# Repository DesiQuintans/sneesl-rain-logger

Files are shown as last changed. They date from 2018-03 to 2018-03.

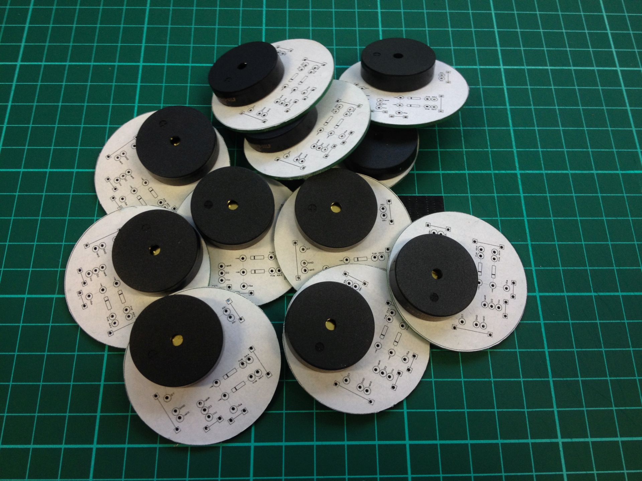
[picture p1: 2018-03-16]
Build notes/Photos/IMG_3371_developed.jpg

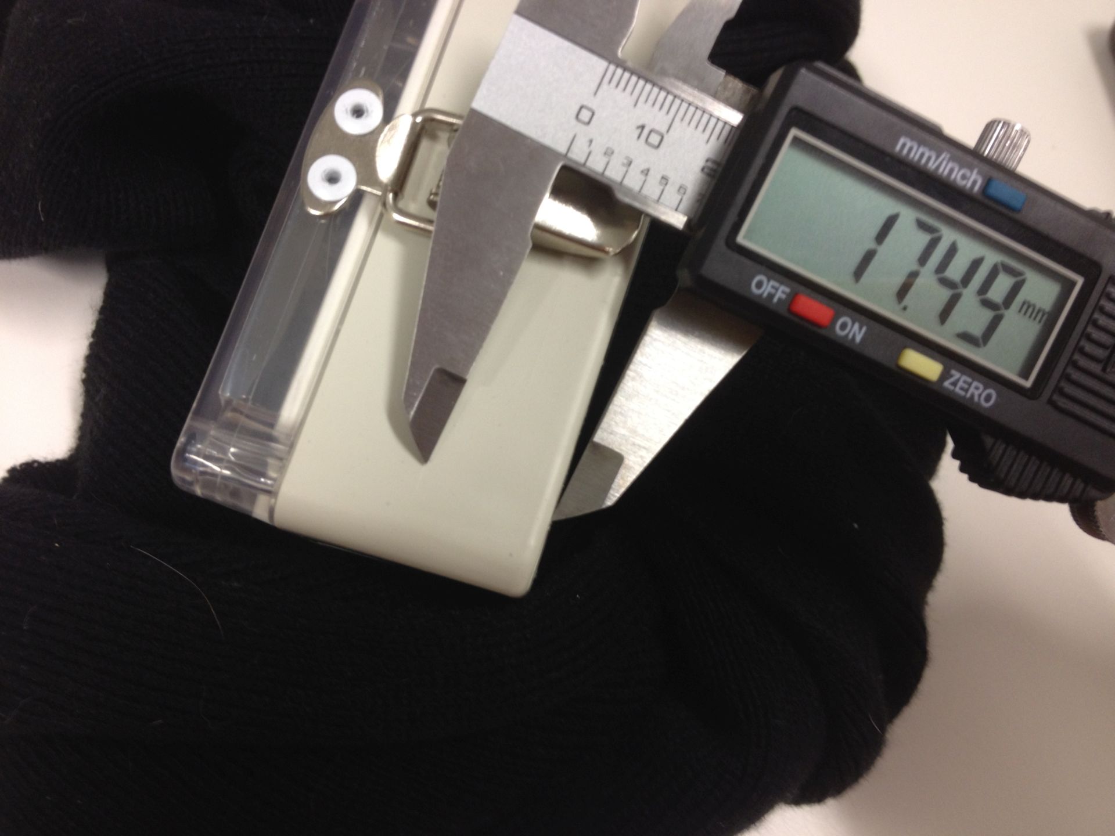
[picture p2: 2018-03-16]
Build notes/Photos/IMG_3365.JPG

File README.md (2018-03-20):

# Sneesl, a TinyDuino-based data-logger for rain collectors

## What is _Sneesl_?

**Sneesl** <sup>1</sup> is a battery-powered data-logging device built on [the TinyDuino plaform](https://tinycircuits.com/pages/tinyduino-overview), designed to record pulses from a tipping-bucket rain collector. These rain collectors are basically large funnels that drain into two small scoops, set back-to-back on a central pivot. When the scoop is full, it tips over and empties itself, raising the other scoop so that it can fill up. The 'tipping over' motion passes a magnet over a reed switch, which is detected and recorded by Sneesl.

Notes and BOM for building a Sneesl data-logger can be found in `Building Sneesl.md`.

Information about how Sneesl works and what kind of data it outputs can be found in `Using Sneesl.md`.

## License and citation

I dedicate Sneesl to the public domain. If you use it for scientific work, please cite:

> Quintans, DJ 2015. Sneesl: An Arduino-based data-logger for rain collectors. Microprocessor software. https://github.com/DesiQuintans/sneesl-rain-logger. doi:10.5281/zenodo.1204674

## Features that Sneesl has

- **6+ months battery life from easy-to-find AA batteries.** It takes 6 batteries in a parallel 3×2 configuration for redundancy. In practice I have sometimes left Sneesl in the field for 9+ months, but I prefer to maintain them more regularly.
- **Data storage on microSD.** MicroSD cards are relatively cheap and are reliable for field use. They can be read in the field using a tablet or laptop, so you can pull down the data without having to bring the logger back to the lab or having to use an expensive reader.
- **Integrated battery life checks.** Sneesl ensures that the battery's voltage is stable enough to safely write data to the SD card. It also records battery life as part of the logging process.
- **Power-On Self-Test.** Sneesl uses a buzzer to warn you if something is wrong (e.g. SD card inserted incorrectly, battery voltage low, unknown problem with the circuit), so that you know the logger is okay before you leave the field site.
- **Input-agnostic pulse counting.** If you have any kind of sensor that uses a switch closure as the response, Sneesl can log it.
- **Timed events.** Sneesl does its logging at regular intervals using a real-time clock, so you can modify it to do things like read a humidity/temperature sensor regularly too.

## Features that Sneesl *does not* have

- Since the number of input channels on an Arduino is limited, Sneesl is not the best choice for multiplexing lots of sensors.
- Sneesl could probably do remote monitoring by using a phone or GSM module to transmit information, but I have not tried to actually implement it here.

## Resources included in this repository

- `Build notes/` contains information about actually building Sneesl.
  - `Bill of materials/` contains a parts list with approximate prices.
  - `Circuits/` has the circuit diagrams. Always use the newest one.
  - `Digital logbook/` is mostly me talking to myself inside text files throughout the development process.
  - `Photos/` has unsorted photos of the development, testing, and assembly process.
- `Firmware/` contains the Arduino code for the loggers.
  - `08_LoggerV8/` is a version of `V7` that has some changes to its comments and formatting.
  - `07_LoggerV7/` is the version I have deployed in the field.
  - `06_LoggerV6/`
  - `05_LoggerV5/`
  - `04_Datalogger_TinyDuino/`
  - `03_BareMetal_TinyDuino/`
  - `02_BareMetal_TD_2/`
  - `01_Datalogger/` is the first version, it ran on $1 Arduino Nano clones with extra modules.
- `_Bench testing/` has enclosure tests, visualisations of data, and battery life predictions.
- `_Scratchpad/` contains code that I used during Sneesl's development process.
  - `INTERRUPTS/` was used for prototyping the wake-up process.
  - `LOW POWER/` was used for prototyping the deep-sleep process.
  - `RTC/` is used to set and get Real-Time Clock modules.
  - `SD/` was for testing different SD card readers before I settled on TinyDuino.
  - `SENSORS/` is test code for photocells (to record brightness) and DHT11 sensors (temperature and humidity) which I omitted from the production run of Sneesl.

---

1: _Sneesl_ is [a Scottish word for raining lightly](http://scottishsceptic.co.uk/2014/11/28/scots-more-words-for-rain-than-eskimos-for-snow/).

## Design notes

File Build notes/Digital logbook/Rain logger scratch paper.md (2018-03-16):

# Logging rain gauge #project

## Use case ##
This device will be placed in the field and allowed to log rain data for at least 1 year and a maximum of 3 years.

## Requirements ##
1. Uses a common battery type like AA or 9 V, allowing for global field resupply.
2. Has a battery life of at least one year.
3. Records rainfall in mass/hour (1 mm == 1 kg per m^2 per hour). The recommended resolution of 0.2 mm is therefore 200 mL per hour.
4. Chassis and moving parts built from off-the-shelf materials with a minimum of hand-working.

## Mathing it up ##
For a 20 cm funnel:

      π x r^2
    = π x 0.1^2 m
    = 0.0314159 m^2 funnel area.

      1 m^2 / funnel area
    = 31.8309886 scaling factor (# funnels inside 1 m^2)

By multiplying a list of potential tipping weights with my scaling factor above, we can find how many mm of rain each bucket tip records. With a 20 cm funnel, 1 mm of rain roughly corresponds with a tip weight of 32 g. With a 10 cm funnel, it corresponds to 8 g (exact numbers in spreadsheet).

## Prototype materials list ##

### From the dollar store ###
| Qty | Item                           | Cost (AUD) |
|-----|--------------------------------|-----------:|
| 1   | Smart-Link 'Store Jar' large   | 2.50       |
| 1   | SAS Automotive 4 pc funnel set | 2.00       |
| 1   | Homeware Hardware 20 cm funnel | 2.00       |
| 2   | Party Central 4 pk candy scoop | 6.00       |
| 1   | Eagiestar 'Epoxy Steel'        | 2.00       |
|     |                                |            |
|     |                      **Total** | **14.50**  |

### From Bunnings ###
| Qty | Item                        | Cost (AUD) |
|-----|-----------------------------|-----------:|
| 1   | 36" of 3/16" threaded rod   | 03.00      |
| 1   | 3/16" bolt and nut 22 pc set| 04.00      |
| 1   | 3/16" brass washer 25 pc set| 03.32      |
|     |                             |            |
|     |                   **Total** | **10.32**  |

## Equipment list ##

### From the dollar store ###
| Qty | Item                | Cost (AUD) |
|-----|---------------------|-----------:|
| 1   | Butane pencil torch | 06.00      |
| 1   | Mini hacksaw        | 03.00      |
| 1   | Mini hacksaw blades | 02.00      |
|     |                     |            |
|     | **Total**           | **11.00**  |

## Order of actions ##
1. Cut off the bottom of the jar with a standard disposable-blade cutter. Discard cut-off.
2. Cut off the handles from two candy scoops with mini hacksaw. File the cut down until level with the scoop body. Discard cut-off handles.
3. Scoop bodies need to be joined to make the double-sided bucket. I'll try Plastimake. A hole for the pivot axle can also be made inside the Plastimake, combining two jobs into one.
    1. First, make a template to ensure that the scoops can be joined at a repeatable angle (40°). Cut three squares from corrugated cardboard, cut a 50° wedge out of each square, and then glue them all face-to-face with epoxy. Cover the cut faces with duct tape; this is your spacer mould.
    1. Soften 5 grams of Plastimake in boiling water. When soft, place it into newly-boiled water to get it as hot as possible. Quickly fold it into a cube, then force the cube into the mould to produce a wedge of Plastimake.
    1. While still soft, push a large nail through the Plastimake wedge from both sides, wiggling the nail to enlarge the hole. This is the hole for the axle.
4. When the wedge is completely solidified, drill out the hole to fit your axle loosely.
5. Soften the sides of the wedge by dipping briefly in boiling water, then press-fit onto the scoops to make the shape of the wedge conform to the shape of the scoop. If desired, the bond can be made stronger with epoxy.

**Wrong turn:** This design seems easy when you're looking at a bunch of scoops, but it's actually really tough to get the scoops centered and place the axle hole uniformly and so on. It took me basically 4 hours to figure out the scoops. Tomorrow I will buy some aluminum sheet (or some cans of soft drink!) and just scratch-make the bucket assembly.

**Another wrong turn:** The jar I bought is also too small. I will grab a PVC pipe and cap tomorrow too.

## Quick reference for rain logger maths ##

### Heaviest one-day rainfall in the world ###
2,493 mm (12,465 0.2 mm bucket tips, ~ 9 per min)

### Heaviest one-day rainfall in the Blue Mountains ###
285 mm (1,425 0.2 mm bucket tips, ~ 1 per min)

### SD card write time ballpark ###
Let's call it 0.01 ms to write 1 byte. Therefore the data string:

    2015-03-21T15:26:47    540\n(24 bytes)

Can be written in 0.24 ms.

### Milliseconds in 1 hour ###
3,600,000 ms

### List of power draws ###

| Board                  | State       | Current draw (mA) |
|------------------------|-------------|------------------:|
| Pro Mini               | Running     | 16.00             |
|                        | Sleeping    | 0.48              |
| MicroSD module         | Writing     | 1.47              |
|                        | Sleeping    | 1.34              |
| Real-Time Clock module | Reading     | ?                 |
|                        | Sleeping    | 1.70              |
| Fudge factor           | All states  | 1.00              |
|                        |             |                   |
| **Total**              | **Running** | **20.17**         |
|                        | **Sleeping**| **4.52**          |

The heaviest rain ever gave 540 tips per hour. At 0.23 ms per tip, that's 0.0000345 of each hour writing at 20.17 mA. That leaves 0.9999655 of each hour doing nothing at 4.52 mA.

Therefore, each hour drains:

			0.000695865 mA per hour writing
			4.519844060 mA per hour idling
	TOTAL = 4.520539925 mA per hour

Therefore, a 2400 mAh alkaline battery gives 530 hours of perfect operation (22 days). The numbers are basically identical for the Blue Mountains rainfall record.

So the biggest drain here is not the time spent running the program, but the time spent sleeping. Therefore my efforts should concentrate on getting idle drain as low as possible.

## Data logger costing ##

| Qty | Item                   | Supplier     |  Cost (AUD) |
|-----|------------------------|--------------|------------:|
| 12  | Davis rain collector   | DavisNet     |     1335.96 |
| 12  | AA battery holder      | LittleBird   |       12.96 |
| 12  | 5 V step-up module     | eBay         |       47.16 |
| 12  | Arduino Pro Mini 5 V   | LittleBird   |      141.00 |
| 12  | 5 x 7 cm proto board   | eBay         |       35.88 |
| 12  | Real-time clock module | eBay         |       44.04 |
| 12  | MicroSD module         | eBay         |       63.24 |
| 12  | 4 GB microSD card      | eBay         |       59.28 |
| 12  | Reed switch module     | eBay         |       45.72 |
| 12  | 64 x 58 x 35 mm box    | LittleBird   |       71.40 |
| 36  | Duracell AA batteries  | eBay         |       29.99 |
|     |                        |              |             |
|     |                        | **Total**    | **1886.63** |
|     |                        | **Fudged**   | **2000.00** |
|     |                        | **Per unit** |  **166.67** |

## Data logger flow ##

1.	Watchdog timer starts (poll every 6 minutes).
2.	Arduino goes to sleep.
3.	Water bucket tips, and a magnet on the bucket sweeps across a reed switch. Reed switch is connected to voltage, and to a digital input pin set up to interrupt sleep.
4.	When the reed switch closes, the digital pin is set high.
5.	Arduino wakes up due to high interrupt pin.
6.	Arduino increments an internal counter (TipCounter), and then goes back to sleep as quickly as possible.
7.	Meanwhile, watchdog timer is asking every 8 minutes:
	1. Does the RTC say that 1 hour has elapsed?
	2. If no, go back to sleep.
	3. If yes:
	    - Write TipCounter to the SD card with the date and time.
	    - Set TipCounter = 0
	    - How many seconds off from the hour is the watchdog? Set the next watchdog timers shorter to sync them.
	    - Go back to sleep.

## Things to do for data logger ##

### For 6 April 2015 ###

- ☑ Learn how to write to microSD.
	- Write:	SD	→	ReadWrite
- ☑ Learn how to set and get RTC.
	- Set:	Time	→	TimeSerial
	- Get:	DS1307RTC	→	ReadTest
- ☒ Learn how to use reed switch to set a pin high.
	- That actually doesn't work --- you need to set the pin low.
- ☑ Learn how to put Arduino to sleep and wake it up with the reed switch.
- ☑ Learn how to use a watchdog timer.
- ☑ Learn how to run an Arduino from 2x AA batteries.
- ☑ Learn how to run RTC from 2x AA batteries.
- ☑ Learn how to write to microSD from 2x AA batteries.

### For 10 April 2015 ###

- ☐ Learn how to measure milliamps with my cheapo multimeter.
	- Ahaha I blew the fuse, that's why I was having trouble.
	- ☑ Make a fixed-voltage power regulator to help me calculate current.
		- I made one with an LM317, Vout= 5.04V, R1=330R, R2=1000R.
- ☐ Experiment with different sleep modes to see if my code still works.
- ☑ Solder headers onto Arduino Pro Mini and Nanos.
- ☐ Transplant modules onto Pro Mini and see if everything works.
- ☐ Design protoboard layout.

## Data logger pinout ##

|         | Module | Arduino |
|---------|--------|---------|
| RTC     |        |         |
|         | Gnd    | GND     |
|         | VCC    | 5V      |
|         | SDA    | A4      |
|         | SCL    | A5      |
|         |        |         |
| MicroSD |        |         |
|         | Gnd    | GND     |
|         | VCC    | 5V      |
|         | MISO   | D12     |
|         | MOSI   | D11     |
|         | SCK    | D13     |
|         | CS     | D10     |

## File naming scheme ##

File names need to be 8 characters or fewer, which is poo. But anyway:

    123456789
    ---------
    20150410

A condensed date naming scheme works, I think, because of my backup strategy:

## Backup strategy ##

I will have one large log (LOGFILE.CSV) where all of my data is written. Every day, the contents of LOGFILE.CSV get dumped into a new file named with the YYYYMMDD.CSV scheme. If LOGFILE.CSV gets corrupted, then the daily dumps might still be alright!

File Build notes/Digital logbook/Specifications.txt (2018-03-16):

# Logging rain gauge #project

## Use case ##
This device will be placed in the field and allowed to log rain data for at least 1 year and a maximum of 3 years.

## Requirements ##
1. Uses a common battery type like AA or 9v, allowing for global field resupply.
2. Has a battery life of at least one year.
3. Records rainfall in mass/hour (1mm == 1kg per m^2 per hour). The recommended resolution of 0.2mm is therefore 200 mL per hour.
4. Chassis and moving parts built from off-the-shelf materials with a minimum of hand-working.

## Mathing it up ##
For a 20 cm funnel:

      π x r^2
    = π x 0.1^2 m
    = 0.0314159 m^2 funnel area.

      1 m^2 / funnel area
    = 31.8309886 scaling factor (# funnels inside 1 m^2)

By multiplying a list of potential tipping weights with my scaling factor above, we can find how many mm of rain each bucket tip records. With a 20cm funnel, 1 mm of rain roughly corresponds with a tip weight of 32 g. With a 10cm funnel, it corresponds to 8 g (exact numbers in spreadsheet).

## Prototype materials list ##

### From the dollar store ###
| Qty | Item                           | Cost (AUD) |
|-----|--------------------------------|-----------:|
| 1   | Smart-Link 'Store Jar' large   | 2.50       |
| 1   | SAS Automotive 4pc funnel set  | 2.00       |
| 1   | Homeware Hardware 20cm funnel  | 2.00       |
| 2   | Party Central 4pk candy scoop  | 6.00       |
| 1   | Eagiestar 'Epoxy Steel'        | 2.00       |
|     |                                |            |
|     |                      **Total** | **14.50**  |

### From Bunnings ###
| Qty | Item                        | Cost (AUD) |
|-----|-----------------------------|-----------:|
| 1   | 36" of 3/16" threaded rod   | 03.00      |
| 1   | 3/16" bolt and nut 22pc set | 04.00      |
| 1   | 3/16" brass washer 25pc set | 03.32      |
|     |                             |            |
|     |                   **Total** | **10.32**  |

## Equipment list ##

### From the dollar store ###
| Qty | Item                | Cost (AUD) |
|-----|---------------------|-----------:|
| 1   | Butane pencil torch | 06.00      |
| 1   | Mini hacksaw        | 03.00      |
| 1   | Mini hacksaw blades | 02.00      |
|     |                     |            |
|     | **Total**           | **11.00**  |

## Order of actions ##
1. Cut off the bottom of the jar with a standard disposable-blade cutter. Discard cut-off.
2. Cut off the handles from two candy scoops with mini hacksaw. File the cut down until level with the scoop body. Discard cut-off handles.
3. Scoop bodies need to be joined to make the double-sided bucket. I'll try Plastimake. A hole for the pivot axle can also be made inside the Plastimake, combining two jobs into one.
    1. First, make a template to ensure that the scoops can be joined at a repeatable angle (40°). Cut three squares from corrugated cardboard, cut a 50° wedge out of each square, and then glue them all face-to-face with epoxy. Cover the cut faces with duct tape; this is your spacer mould.
    1. Soften 5 grams of Plastimake in boiling water. When soft, place it into newly-boiled water to get it as hot as possible. Quickly fold it into a cube, then force the cube into the mould to produce a wedge of Plastimake.
    1. While still soft, push a large nail through the Plastimake wedge from both sides, wiggling the nail to enlarge the hole. This is the hole for the axle.
4. When the wedge is completely solidified, drill out the hole to fit your axle loosely.
5. Soften the sides of the wedge by dipping briefly in boiling water, then press-fit onto the scoops to make the shape of the wedge conform to the shape of the scoop. If desired, the bond can be made stronger with epoxy.

**Wrong turn:** This design seems easy when you're looking at a bunch of scoops, but it's actually really tough to get the scoops centered and place the axle hole uniformly and so on. It took me basically 4 hours to figure out the scoops. Tomorrow I will buy some aluminum sheet (or some cans of soft drink!) and just scratch-make the bucket assembly.

**Another wrong turn:** The jar I bought is also too small. I will grab a PVC pipe and cap tomorrow too.

## Quick reference for rain logger maths ##

### Heaviest one-day rainfall in the world ###
2,493 mm (12,465 0.2 mm bucket tips, ~ 9 per min)

### Heaviest one-day rainfall in the Blue Mountains ###
285 mm (1,425 0.2mm bucket tips, ~ 1 per min)

### SD card write time ballpark ###
Let's call it 0.01 ms to write 1 byte. Therefore the data string:

    2015-03-21T15:26:47    540\n(24 bytes)

Can be written in 0.24 ms.

### Milliseconds in 1 day ###
3,600,000 ms

### List of power draws ###

| Board                  | State       | Current draw (mA) |
|------------------------|-------------|------------------:|
| Pro Mini               | Running     | 16.00             |
|                        | Sleeping    | 0.48              |
| MicroSD module         | Writing     | 1.47              |
|                        | Sleeping    | 1.34              |
| Real-Time Clock module | Reading     | ?                 |
|                        | Sleeping    | 1.70              |
| Fudge factor           | All states  | 1.00              |
|                        |             |                   |
| **Total**              | **Running** | **20.17**         |
|                        | **Sleeping**| **4.52**          |

The heaviest rain ever gave 540 tips per hour. At 0.23 ms per tip, that's 0.0000345 of each hour writing at 20.17 mA. That leaves 0.9999655 of each hour doing nothing at 4.52 mA.

Therefore, each hour drains: 

			0.000695865 mA per hour writing
			4.519844060 mA per hour idling
	TOTAL = 4.520539925 mA per hour

Therefore, a 2400 mAh alkaline battery gives 530 hours of perfect operation (22 days). The numbers are basically identical for the Blue Mountains rainfall record.

So the biggest drain here is not the time spent running the program, but the time spent sleeping. Therefore my efforts should concentrate on getting idle drain as low as possible.

## Data logger costing ##

| Qty | Item                   | Supplier     |  Cost (AUD) |
|-----|------------------------|--------------|------------:|
| 12  | Davis rain collector   | DavisNet     |     1335.96 |
| 12  | AA battery holder      | LittleBird   |       12.96 |
| 12  | 5V step-up module      | eBay         |       47.16 |
| 12  | Arduino Pro Mini 5V    | LittleBird   |      141.00 |
| 12  | 5 x 7 cm proto board   | eBay         |       35.88 |
| 12  | Real-time clock module | eBay         |       44.04 |
| 12  | MicroSD module         | eBay         |       63.24 |
| 12  | 4GB microSD card       | eBay         |       59.28 |
| 12  | Reed switch module     | eBay         |       45.72 |
| 12  | 64 x 58 x 35 mm box    | LittleBird   |       71.40 |
| 36  | Duracell AA batteries  | eBay         |       29.99 |
|     |                        |              |             |
|     |                        | **Total**    | **1886.63** |
|     |                        | **Fudged**   | **2000.00** |
|     |                        | **Per unit** |  **166.67** |

## Data logger flow ##

1.	Watchdog timer starts (poll every 6 minutes).
2.	Arduino goes to sleep.
3.	Water bucket tips, and a magnet on the bucket sweeps across a reed switch. Reed switch is connected to 	voltage, 
        and to a digital input pin set up to interrupt sleep.
4.	When the reed switch closes, the digital pin is set high.
5.	Arduino wakes up due to high interrupt pin.
6.	Arduino increments an internal counter (TipCounter), and then goes back to sleep as quickly as possible.
7.	Meanwhile, watchdog timer is asking every 8 minutes:
	1. Does the RTC say that 1 hour has elapsed?
	2. If no, go back to sleep.
	3. If yes:
	    - Write TipCounter to the SD card with the date and time.
	    - Set TipCounter = 0
	    - How many seconds off from the hour is the watchdog? Set the next watchdog timers shorter to sync them.
	    - Go back to sleep.

## Things to do for data logger ##

- ☑ Learn how to write to microSD.
	- Write:	SD	→	ReadWrite
- ☑ Learn how to set and get RTC.
	- Set:	Time	→	TimeSerial
	- Get:	DS1307RTC	→	ReadTest
- ☒ Learn how to use reed switch to set a pin high.
	- That actually doesn't work --- you need to set the pin low.
- ☑ Learn how to put Arduino to sleep and wake it up with the reed switch.
- ☑ Learn how to use a watchdog timer.
- ☑ Learn how to run an Arduino from 2x AA batteries.
- ☑ Learn how to run RTC from 2x AA batteries.
- ☑ Learn how to write to microSD from 2x AA batteries.

### For 10 April 2015: ###
- ☐ Learn how to measure milliamps with my cheapo multimeter.
- ☐ Experiment with different sleep modes to see if my code still works.
- ☐ Solder headers onto Arduino Pro Mini.
- ☐ Transplant modules onto Pro Mini and see if everything works.
- ☐ Design protoboard layout.

## Data logger pinout ##

|         | Module | Arduino |
|---------|--------|---------|
| RTC     |        |         |
|         | Gnd    | GND     |
|         | VCC    | 5V      |
|         | SDA    | A4      |
|         | SCL    | A5      |
|         |        |         |
| MicroSD |        |         |
|         | Gnd    | GND     |
|         | VCC    | 5V      |
|         | MISO   | D12     |
|         | MOSI   | D11     |
|         | SCK    | D13     |
|         | CS     | D4      |

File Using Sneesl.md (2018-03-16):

# Using and maintaining Sneesl

## Diagnostic buzzer sounds

### Error sounds

**3 beeps, each the same pitch**
Low battery voltage, or circuit error. Replace the batteries and/or check the circuit for loose or shorted wires.

**2 beeps, one short and one long, each the same pitch**
SD card access error. The card couldn't be accessed or written to. Remove the batteries and then try removing and reinserting the SD card.

### All-okay sounds

**Four notes, rising pitch**
Power-On Self-Test found no problems, the logger is now ready for input. Tip the buckets manually to confirm that they move freely before leaving the site.

**Single beeps**
Played when a bucket tip is detected and added to the running count. A higher-pitched version is played when the running count is recorded to the logfile.

## Logged data format

By default, Sneesl writes to the logfile hourly in this format:

| Time                | Tips | mV   | Event  |
|---------------------|------|------|--------|
| 2016-12-24T12:29:07 | 0    | 4483 | Reboot |
| 2016-12-24T13:00:00 | 0    | 4630 | Normal |
| 2016-12-24T14:00:00 | 0    | 4278 | Normal |
| 2016-12-24T15:00:00 | 3    | 4295 | Normal |
| 2016-12-24T16:00:00 | 7    | 4295 | Normal |
| 2016-12-24T17:00:00 | 34   | 4295 | Normal |
| 2016-12-24T18:00:00 | 16   | 4278 | Normal |
| 2016-12-24T19:00:00 | 3    | 4395 | Normal |
| 2016-12-24T20:00:00 | 0    | 4611 | Normal |
| 2016-12-24T21:00:00 | 0    | 4593 | Normal |

- `Time` is in ISO-8601 format for easy parsing with software.
- `Tips` is the number of bucket tips recorded in the preceding hour. My buckets hold 0.2 mm of rain, so the rainfall experienced between 4 and 5 PM is `34 × 0.2 = 6.8 mm`.
- `mV` is the estimated voltage available at the time of recording. Note that because this is a (very) rough estimation, the values fluctuate quite a bit. This fluctuation is accounted for in Sneesl's voltage checking function.
- `Event` marks the type of log written. _Reboot_ events are written during POST and should be omitted from your results.

## Maintaining Sneesl

- Keep the data loggers dry and sheltered. Mine fit inside the rain collector's housing, which is very convenient.
- Make sure that the wire leading to the data logger does not interfere with the motion of the buckets.
- I had several instances where dust and debris clogged the rain collector and stopped all readings. It pays to check your collectors regularly during the rainy season to make sure this isn't happening.
- Be careful of spiders that make their homes inside the rain collector.
- RTC units can drift by a few minutes over the course of a year. If this is a problem, you should bring in your Sneesl units once a year to update their internal clocks and/or replace the RTC's onboard batteries.

## Program logic

### Power-On Self-Test

1. The user inserts batteries. Sneesl will run on 3x AA batteries, but it is best to provide 6 AA batteries so that there is a redundant power supply option.
2. Sneesl estimates the available battery voltage.
  - If voltage is <3200 mV, the batteries are discharged below an experimentally-derived safety limit. Below this level, the TinyDuino may randomly 'brownout' and reading/writing to the SD card may destroy the stored data.
  - In case of low voltage, Sneesl will use the buzzer to play an insistent error sound (three identical notes, looping). This error sound will also play if there is error in the circuit that interferes with Power-On Self-Test, like a loose wire.
3. If voltage is above the safety limit, Sneesl tries to create a new logfile (if one doesn't exist already) and then tries to write a new observation to the file (marked as a 'Reboot' event).
  - If logfile creation or writing fail, then Sneesl's buzzer will play an SD warning sound (short-long, short-long — imagine it's saying, "Ess Dee! Ess Dee!").
4. Sneesl sets an alarm telling it when to wake up (by default, `RTC.setAlarmRepeat(EVERY_HOUR);`), and then goes into deep sleep to save power.

### In the event of rain

1. If the rain collector's bucket is tipped, the pulse created by the switch wakes Sneesl.
2. Sneesl checks its voltage again, making sure that it is safe to write to the Arduino's onboard memory.
3. The bucket tip is added to a running count.
4. Sneesl goes back to sleep.

### When the alarm goes off

1. The RTC alarm wakes Sneesl.
2. It checks its voltage again to make sure that it is safe to access the SD card.
3. Sneesl records the number of bucket tip events that it counted since the last alarm (marked as a 'Normal' logging event). A confirmation sound is played.
4. The running count is cleared and Sneesl goes back to sleep.

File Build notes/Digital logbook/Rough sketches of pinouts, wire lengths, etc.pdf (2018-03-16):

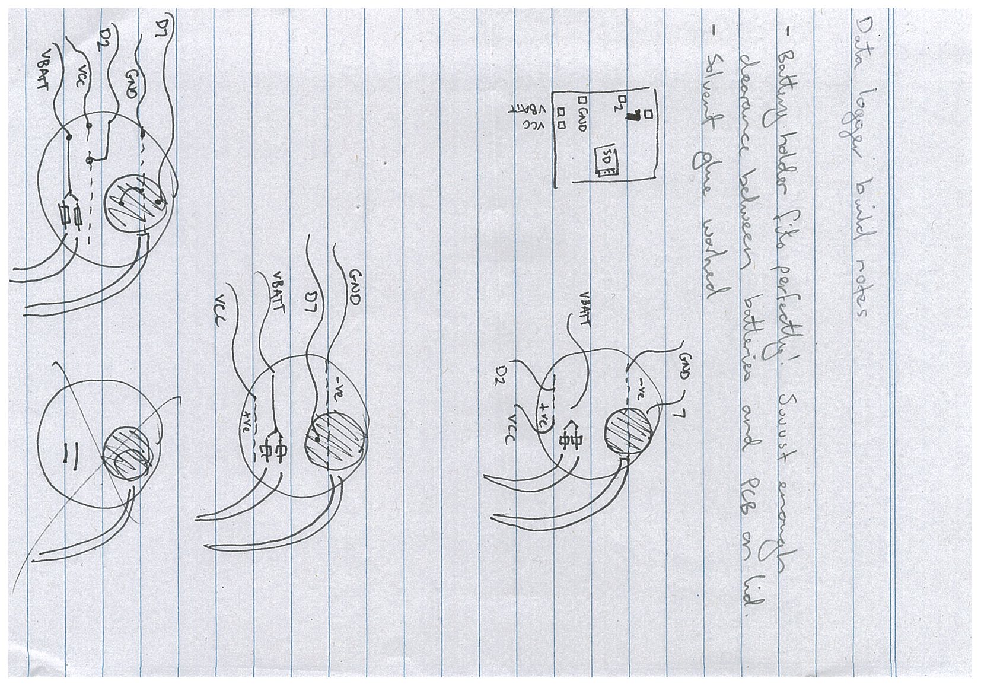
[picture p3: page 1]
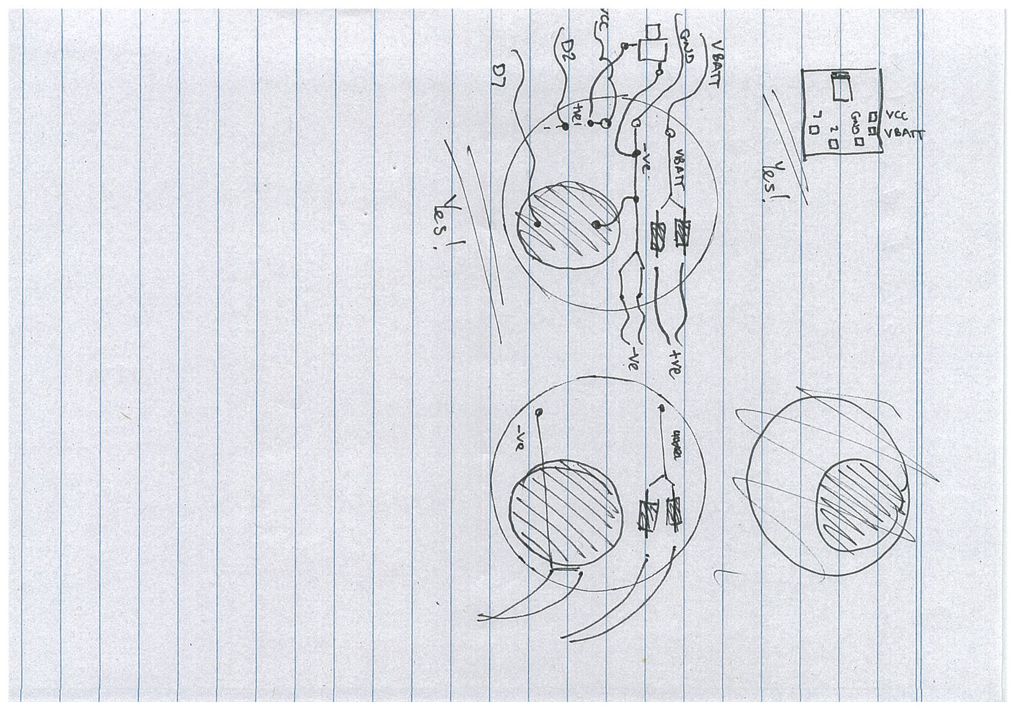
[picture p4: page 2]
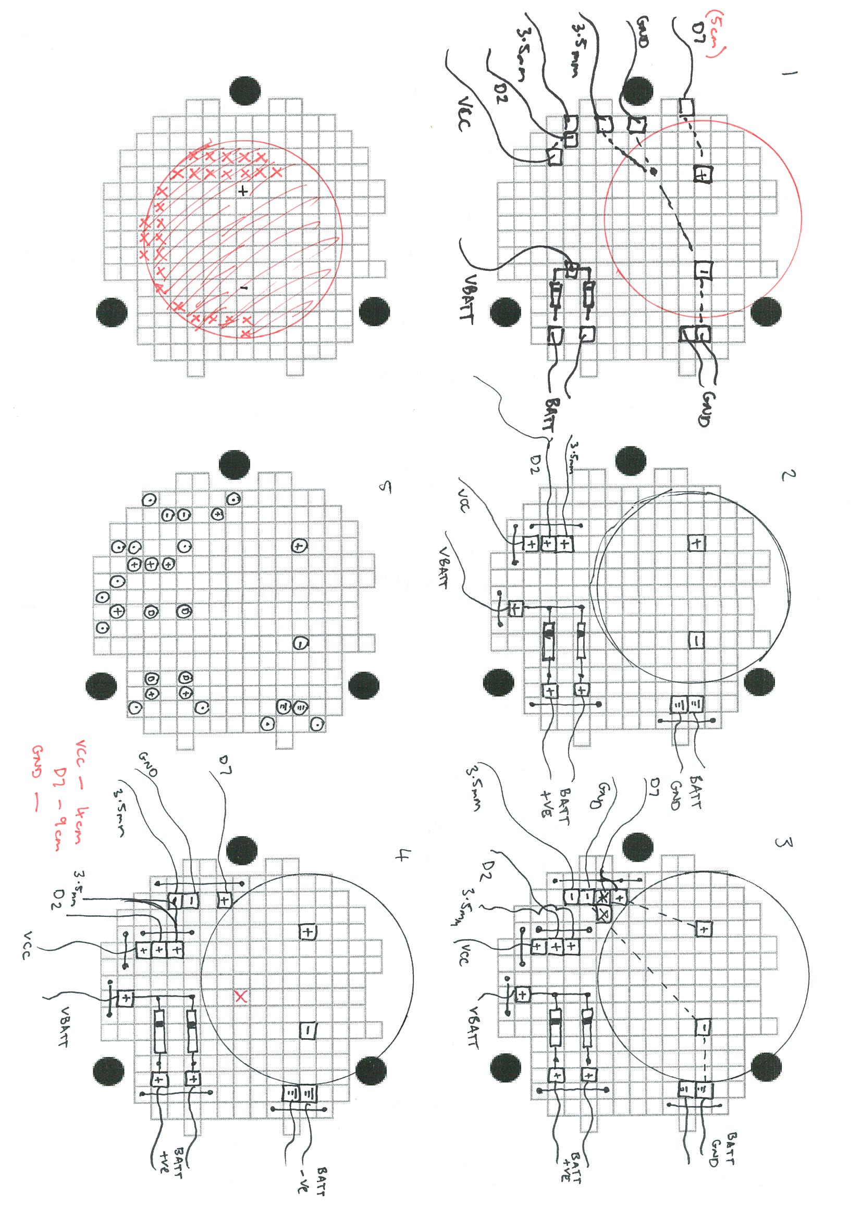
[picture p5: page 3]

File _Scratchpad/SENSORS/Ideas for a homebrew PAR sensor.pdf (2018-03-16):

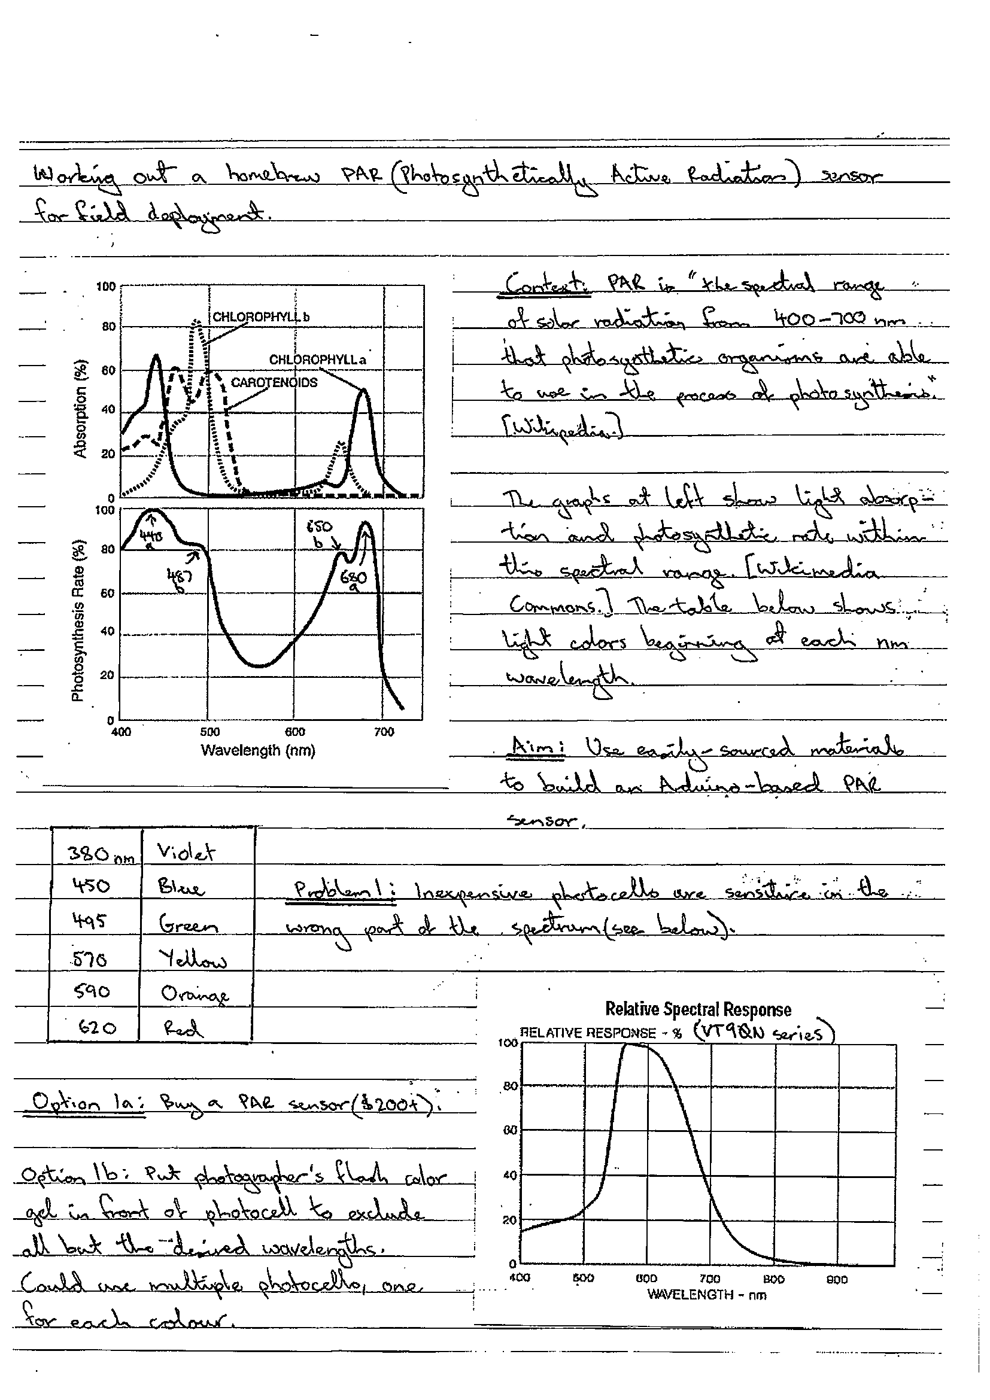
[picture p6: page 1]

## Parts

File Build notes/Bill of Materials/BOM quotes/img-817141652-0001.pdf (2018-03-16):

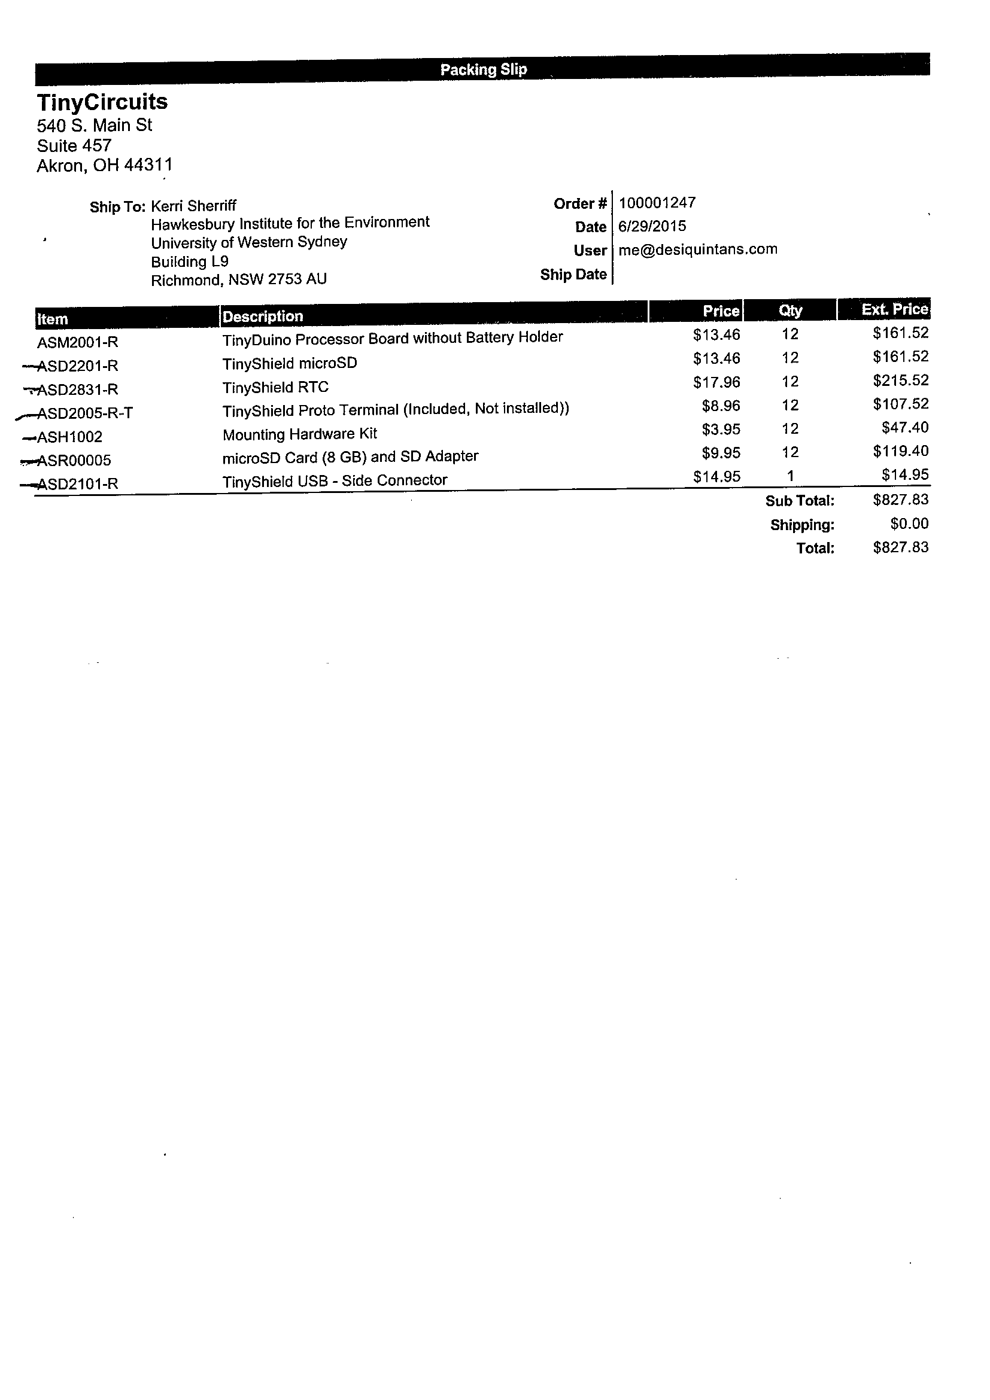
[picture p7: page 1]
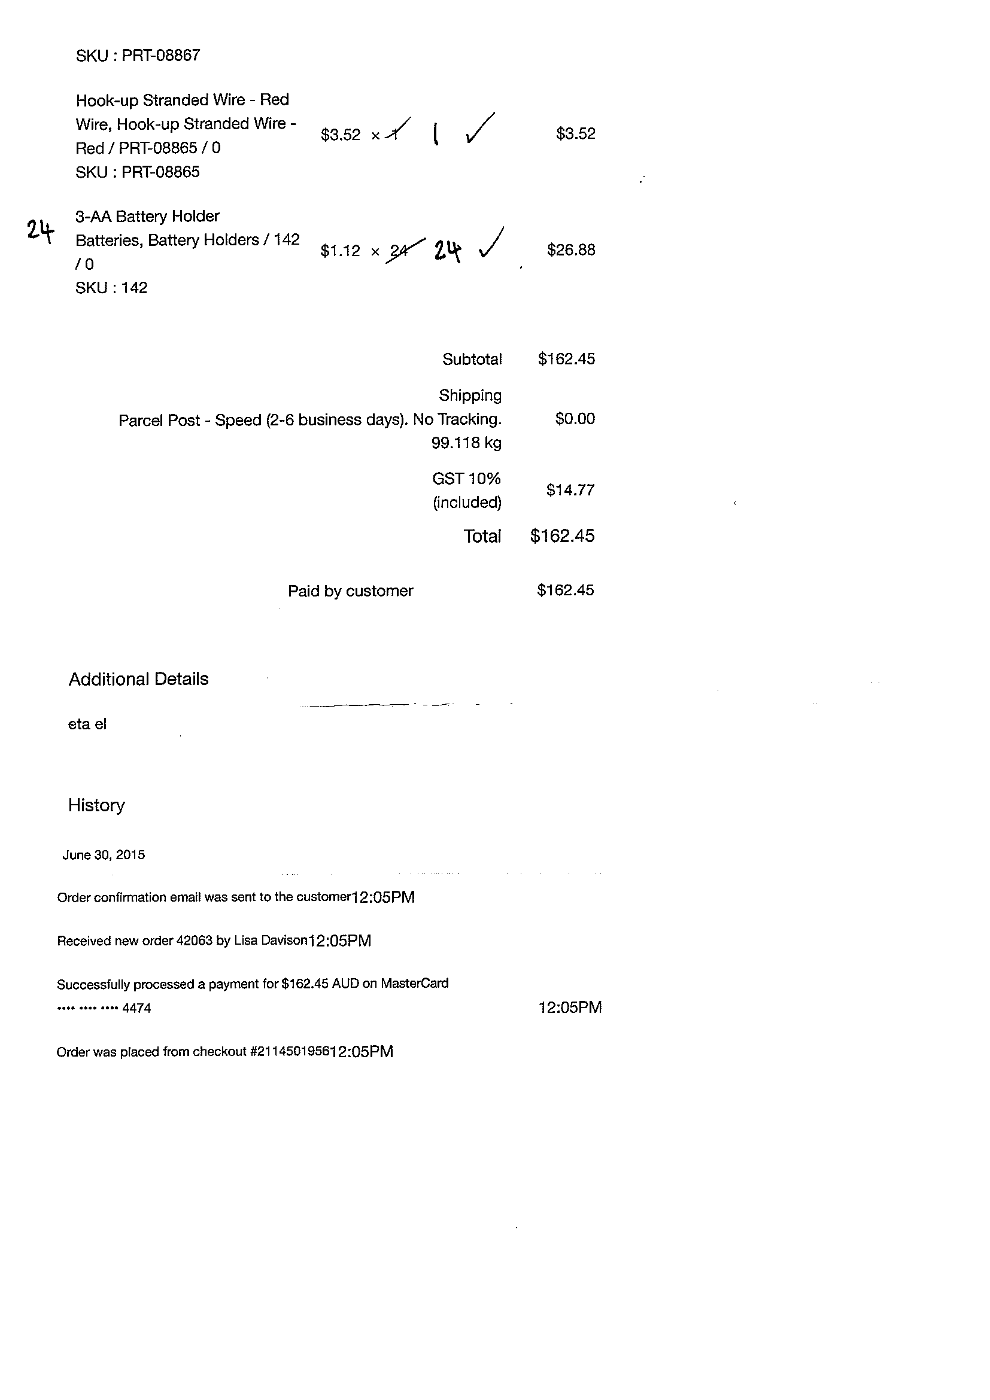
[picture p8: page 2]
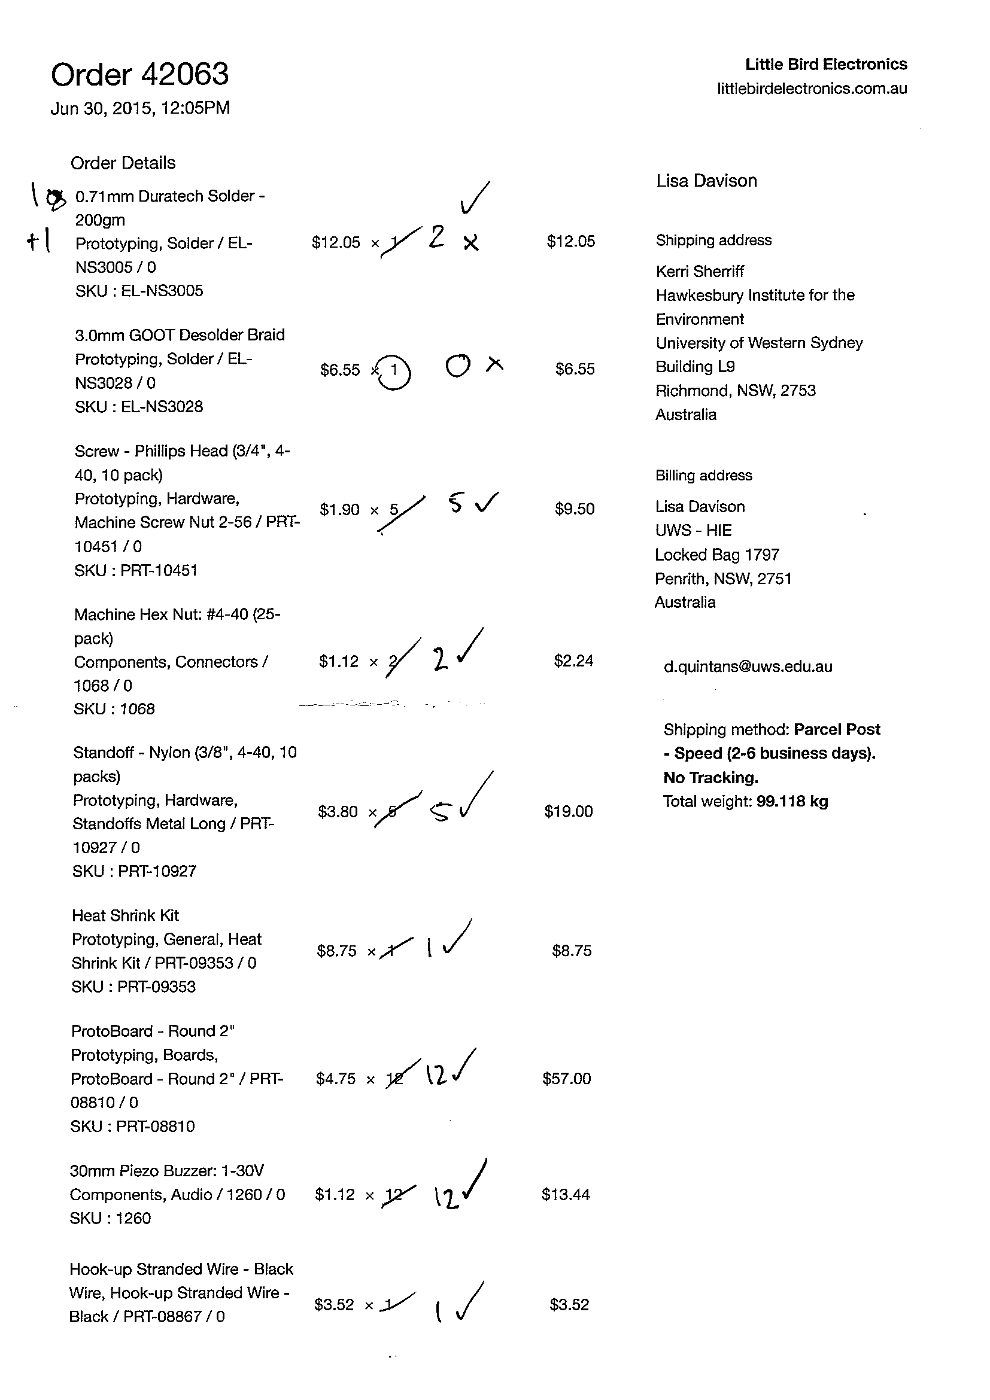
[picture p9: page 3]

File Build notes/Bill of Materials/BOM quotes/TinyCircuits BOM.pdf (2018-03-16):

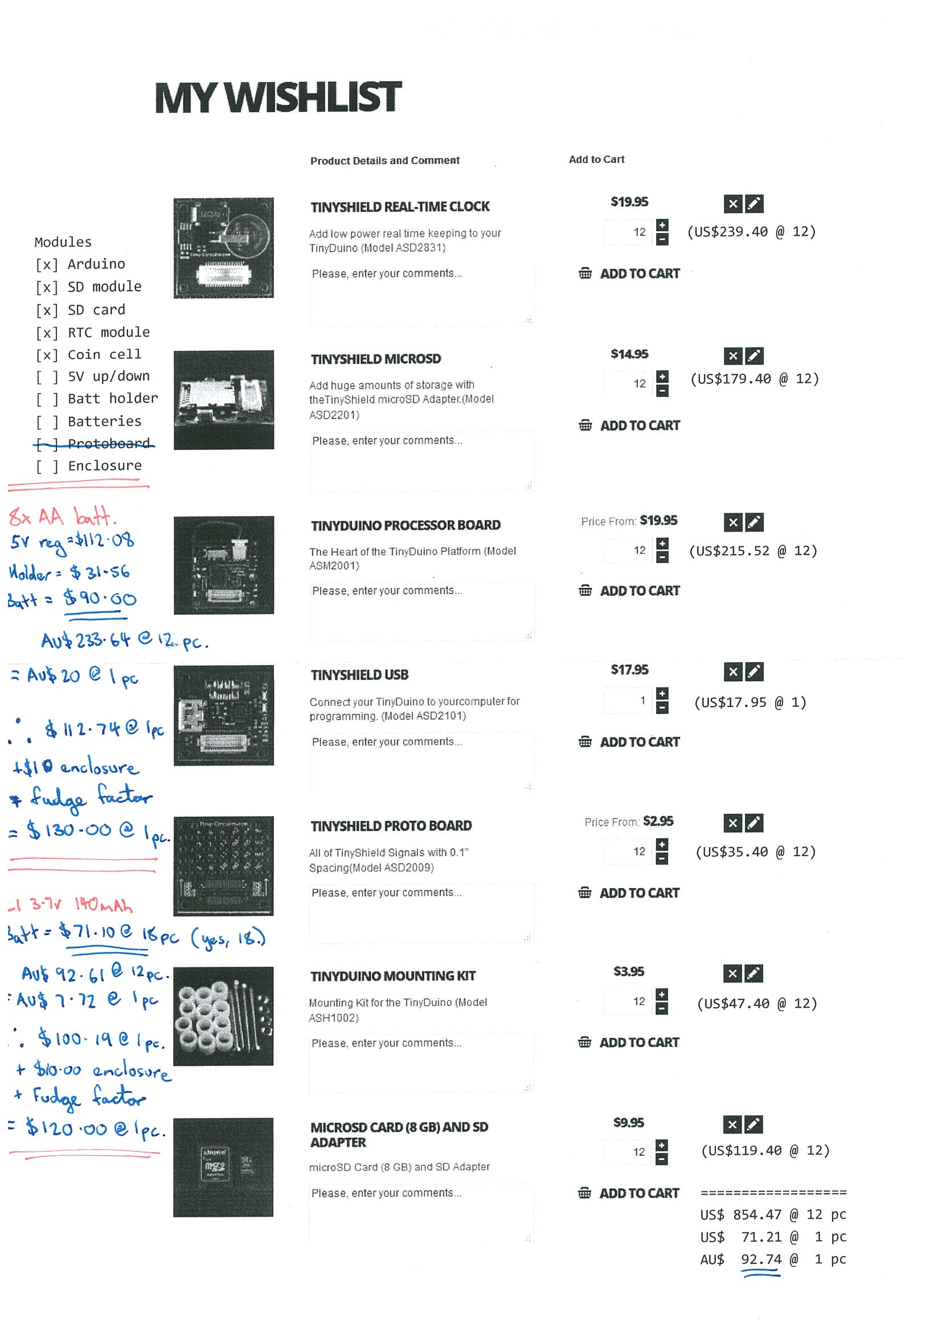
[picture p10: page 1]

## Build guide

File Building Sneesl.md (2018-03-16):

# Building a Sneesl data logger

These notes assume that you have basic experience with assembling and soldering an electronic circuit, as well as connecting and programming an Arduino.

## Materials for 1x Sneesl

| Pieces | Object                                  | Source            | Rounded cost (AUD)   |
| ------ | --------------------------------------- | ----------------- | -------------------- |
|        | **Exterior:**                           |                   |                      |
| 1      | Davis tipping-bucket rain collector     | Davis Instruments | 150.00               |
| 1      | Waterproof enclosure, 100×68×50 mm      | AliExpress        | 3.00                 |
| 1      | Spring-loaded toggle latch, 27 mm       | AliExpress        | 1.00                 |
| 4      | Pop rivets for latch                    | Hardware store    | 1.00                 |
|        |                                         |                   | 155.00 (Total)       |
|        | **TinyDuino modules:**                  |                   |                      |
| 1      | Processor board w/o battery holder      | TinyCircuits      | 14.00                |
| 1      | TinyShield MicroSD                      | TinyCircuits      | 14.00                |
| 1      | TinyShield RTC                          | TinyCircuits      | 18.00                |
| 1      | TinyShield Proto Terminal               | TinyCircuits      | 9.00                 |
| 1      | Mounting hardware kit                   | TinyCircuits      | 4.00                 |
| 1      | MicroSD card (8GB) *                    | TinyCircuits      | 10.00                |
| 1      | TinyShield USB (side connector) *       | TinyCircuits      | 15.00                |
|        |                                         |                   | 84.00 (Total)        |
|        | **Assorted electronics:**               |                   |                      |
| 2      | Diode, 1N5819                           | AliExpress        | 1.00                 |
| 1      | Resistor, 4.7k ohms                     | AliExpress        | 1.00                 |
| 1      | Through-hole piezo buzzer               | AliExpress        | 1.00                 |
| 1      | 3.5 mm jack (male/female panel-mount) * | AliExpress        | 1.00                 |
| 1      | Prototyping board (cut to size)         | AliExpress        | 1.00                 |
| 2      | 3x AA battery holders                   | AliExpress        | 1.00                 |
| 6      | AA batteries (decent ones) *            | Reject Shop       | 2.00                 |
|        |                                         |                   | 8.00 (Total)         |
|        | **Other consumables:**                  |                   |                      |
|        | Solid-core and braided wire             |                   |                      |
|        | Solder                                  |                   |                      |
|        | Soldering braid                         |                   |                      |
|        | Printable adhesive labels               |                   |                      |
|        |                                         |                   | 247.00 (Grand total) |

**Re. microSD cards:** I bought the cards from TinyCircuits so that I didn't have to worry about compatibility or counterfeiting. If you want to source your own SD cards, try to find cards that are 1-16 GB in size, since these tend to be more reliable with Arduinos.

**Re. the TinyShield USB programmer:** You only need to buy one or two of these; the USB programmer is not deployed in the field with the rest of the stack.

**Re. the 3.5 mm jack:** You can use any **normally open** connector you want, I just had a lot of 3.5 mm jacks on hand. You *could* wire the rain collector into the logger directly, but it's very convenient to be able to separate them.

**Re. AA battery holders:** Some holders come with an exposed length of wire at the back, linking the cells together. It's smart to cover this wire with tape so that it doesn't short with anything.

**Re. AA batteries:** I can buy a 50-pack of Eveready AA batteries for $12 from my local Reject Shop branch (it's a seconds store). These batteries haven't leaked in any of my 12 loggers, even when the temperature fluctuates from 0–45 °C. I guess you could use rechargeables, but then you add the mental load of having to make sure the new batteries are properly charged. The downside of using disposable batteries is that every 6 months when I replace the batteries, I am left with 72 batteries that are only one-quarter discharged.

## Circuit diagram

Please see `Build notes/Circuits/` to find circuit diagrams. The .fzz format is openable with [Fritzing](http://fritzing.org). If you don't have Fritzing, you can look at the .png format version.

## Build photos and tips

Please see `Build notes/Photos/` for mixed photos of the build process that could be helpful. If you browse the documents in `Build notes/Digital logbook/` could also be instructive.

## Programming Sneesl

### Library dependencies

- [rocketscream's Low-Power](https://github.com/rocketscream/Low-Power)
- [sridharrajagopal's DSRTCLib](https://github.com/sridharrajagopal/DSRTCLib)

### General notes

You can use the Arduino IDE to program Sneesl.

1. Use `_Scratchpad/RTC/Set_RTC_Time` to set the time on the TinyDuino's RTC (real-time clock) shield. Compile the script and then upload it immediately (because it sets the RTC based on the compile time of the script).
2. Compile and upload the latest Sneesl firmware from `Firmware/`.

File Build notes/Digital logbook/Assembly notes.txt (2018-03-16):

# 11 Aug 2015 #

Things I'm happy with:

	* The battery holder fits perfectly! Juuuuust enough clearance between the top of the batteries and the top of the buzzer on the overturned PCB.
	* The spring clasps are amazeballs. So handy already.
	* The PCB and TinyDuino are sized perfectly to fit into the lid. Mounting with double-sided tape is simple and secure.
	* Using terminal screw-posts is great because the wires can be flattened against the lid. Using pins or soldering them onto the protoshield would make them stick out at least a little.
	* Battery wires on the right side of the PCB is fine. There's a hollow on the right of the battery pack that they can nestle into.

Things I'm neutral about:

	* The wires going from the PCB to the TinyDuino are quite rigid. However, a good side of this is that once the PCB and TinyDuino are mounted, the wires can be pushed down and will stay put by themselves.
	* The TinyDuino is mounted so that the wires make sense, but you need to sort of dig in between the wires coming out of the PCB to get the SD card out. If I flip it 180° the GND and D2 wires would be incredibly short, but the SD card will easy to grab from the edge of the lid.

Things I'm unhappy with:

	* The lid looks uninteresting from the outside because everything is mounted upside-down.
	* The logger label covers the TinyDuino, which is more visually interesting than the PCB (for now).
	* Over-torquing the face screw of the 3.5 mm jack can cause it to shear apart! Do not over-tighten. Countersinking the front face so that the nut sits inside the material should give me a more positive (and glue-able!) attachment.
	* The wires coming off the PCB and to the components in the case body (battery packs and 3.5 mm jack) need to be tidied up with braided cable covering. The battery and 3.5 mm should be done separately, so that the battery packs can be removed independently.
	* The logger reads a tip event whenever something conductive touches the closed 3.5 mm jack's contacts. 
	* Pull-up resistor can probably be removed from the PCB, using the built-in pull-up instead.
	* The 3.5 mm jack needs to be mounted so that it's easier to fit from the inside.
	* The cord for the 3.5 mm jack is too short.

Things to add and change:

	* A silica bag can be placed on the left side, both to cushion the battery pack and prevent movement, as well as to protect the internals. Need to find the indicator silica!
	* Can I mount the PCB right-side-up by using cut-down standoffs? Is it worth it? Maybe for just one photo-op logger?
	* 
		* If I don't mount the PCBs right-way–up, I can move the top-face labels so that they cover the middle of the PCB and make it look less boring.

	* Add braided cable cover to battery and 3.5 mm jack wires — or tidy up in some other way. Short lengths of shrink wrap? Tiny zip ties?
	* 
		* But should not interfere with the battery pack's fit into the enclosure!

	* Can I change the 3.5 mm jack/plug to fix the false readings?
	* 3.5 mm jack cables need to be made as long as the battery pack cables.
	* Countersink the face of the 3.5 mm mounting hole.

# 12 Aug 2015 #

After trying some of the proposed changes:

	* Mounting the PCB right-side-up is not worth it, because it increases complexity and makes an already-cramped build more cramped.
	* Braided cable is a bit of a job, but zip ties or shrink wrap work just fine for binding the wires together.
	* The 3.5 mm plug cannot be changed; it will always trigger when plugging in a jack, regardless of what wiring I try. Will simply catch it during data quality control (filter out <1 mm of rain within an hour).
	* 3.5 mm jack cables are now 15 cm long. They could still stand to be longer, perhaps 20 cm for the one that needs to reach longer.
	* I tried mounting the TinyDuino rotated 180° so that the SD card would be against the edge of the lid, reasoning that this would make it easier to grab. It actually makes it more difficult, because the lid prevents you from getting your finger underneath the card. When the card is adjacent to the PCB, there's enough room to do that.
	* Countersinking the 3.5 mm jacks was unnecessary; Simply super-gluing them into the hole and finger-tightening the locking nut is good enough.

# 31 Aug 2015 #

☑ Mount spring clasps onto boxes.
☑ Drill rain jack mounting holes.
☑ Solder wires to rain jacks, then heatshrink.
☑ Clip mounting studies off the bottoms of the boxes.
☑ Glue 3x AA holders back-to-back.
☑ Make first PCB prototype.
☑ Revise PCB layout and make PCB guide labels.
☑ Affix guide labels to remaining PCBs.
☑ Make changes to Arduino software: logging period and internal pull-up resistor.
☑ Prep battery wires and rain jack wires with short lengths of heatshrink to keep them tidy in the box.
☒ Make breadboard test-bed for PCB components (to test functionality before soldering).
     ☒ Test all battery pack combinations (pack A only, pack B only, both packs in parallel) to ensure they work.
     ☒ Test with rain collector hooked into the circuit.
☑ Populate PCBs with buzzer, diodes, and rails.
☑ Pre-cut wire lengths for PCBs.
☑ Solder all components and wires.
☑ Add strain relief staples.
☐ Assemble TinyDuinos.
☐ Set TinyDuino time.
☐ Program TinyDuinos with newest software.
☐ Hook up PCBs to TinyDuinos, trimming wires to fit.
☑ Glue and screw rain jacks to boxes.

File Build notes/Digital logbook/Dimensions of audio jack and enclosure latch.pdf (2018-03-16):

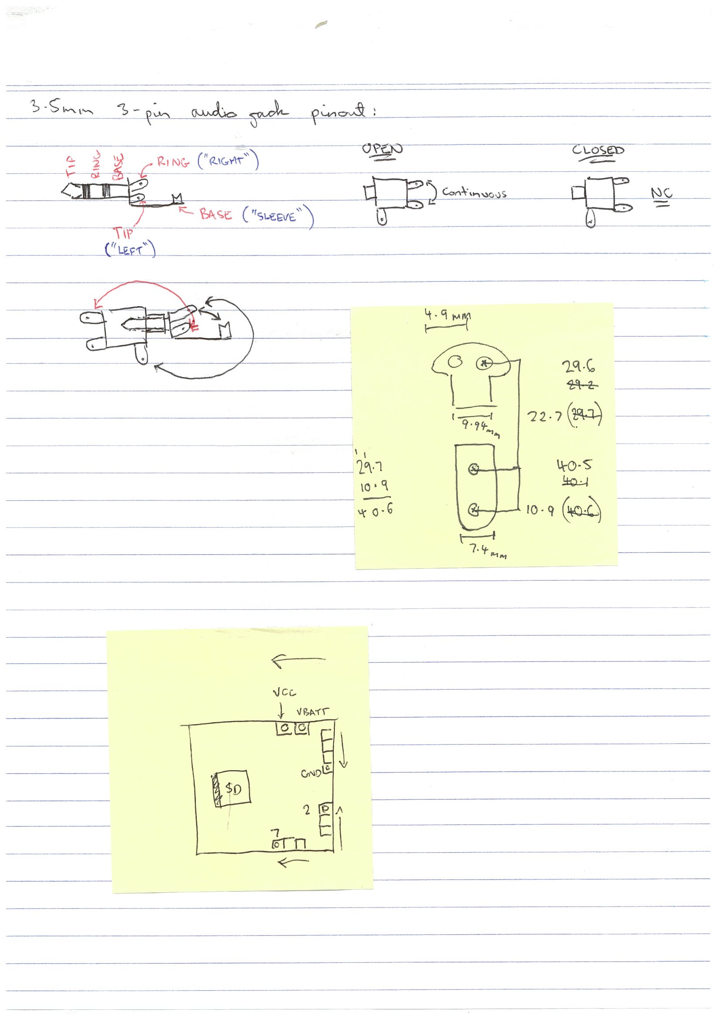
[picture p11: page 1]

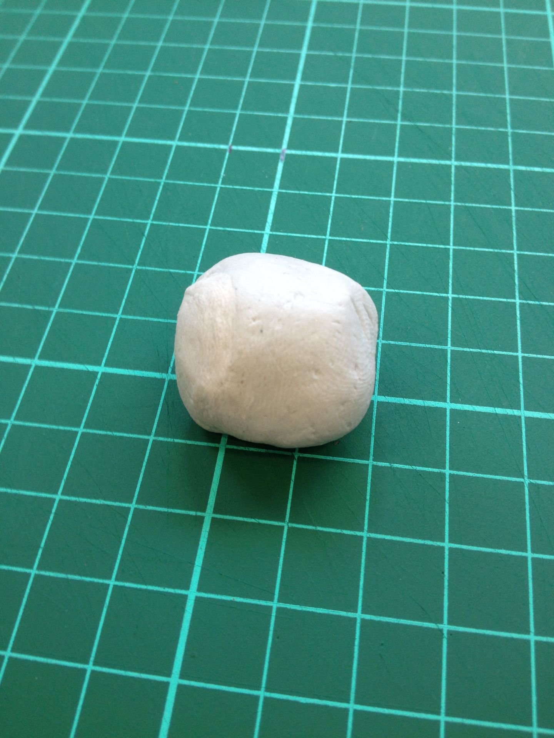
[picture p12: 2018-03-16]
Build notes/Photos/Photo 17-08-2015 11 25 43.jpg

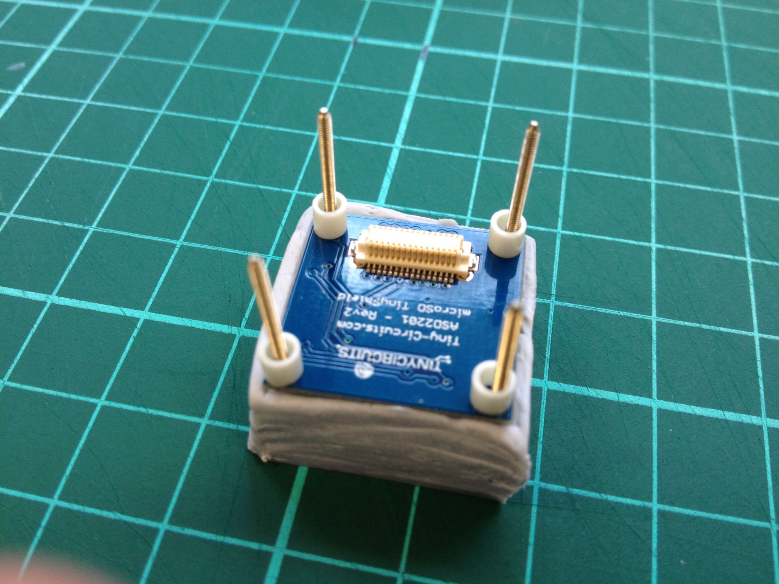
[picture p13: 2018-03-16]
Build notes/Photos/Photo 17-08-2015 11 46 45.jpg

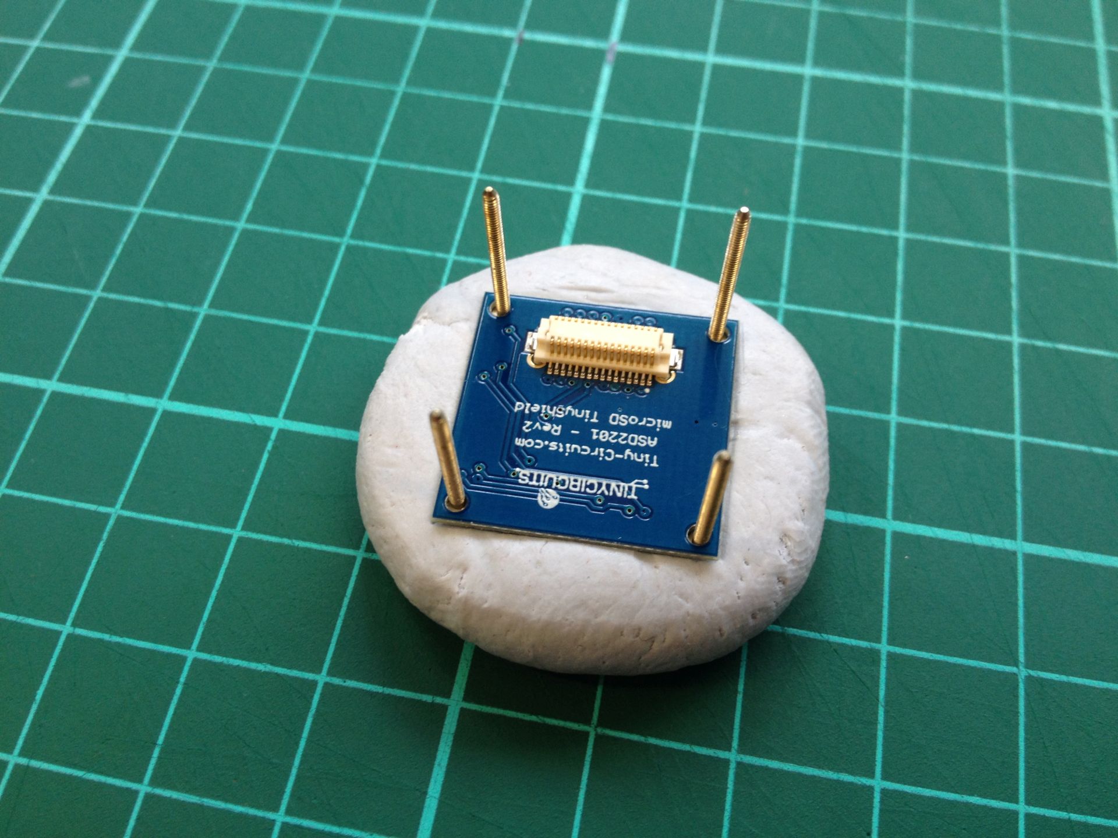
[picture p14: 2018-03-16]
Build notes/Photos/Photo 17-08-2015 11 30 31.jpg

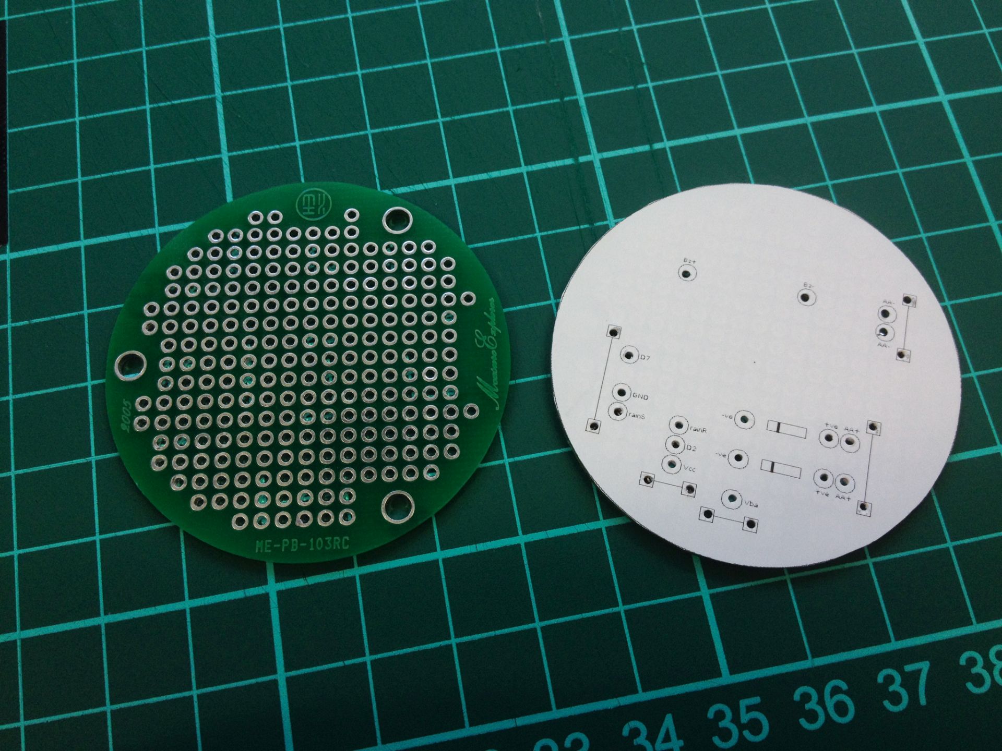
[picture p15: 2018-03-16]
Build notes/Photos/IMG_3372_developed.jpg

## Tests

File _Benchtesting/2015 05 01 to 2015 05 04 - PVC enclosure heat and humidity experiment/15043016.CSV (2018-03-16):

Time | Tips | Hum% | TempC | voltMeasure(V) | readVcc(mV) | Event
2015-04-30T11:45:17 | 0 | 48.00 | 22.00 | 5.08 | 4892 | Rebooted
2015-04-30T11:46:03 | 0 | 38.00 | 23.00 | 5.10 | 4892 | Normal
2015-04-30T11:47:02 | 0 | 40.00 | 22.00 | 5.09 | 4892 | Normal
2015-04-30T11:48:02 | 0 | 40.00 | 22.00 | 5.08 | 4913 | Normal
2015-04-30T11:49:02 | 0 | 39.00 | 23.00 | 5.10 | 4913 | Normal
2015-04-30T11:50:01 | 0 | 39.00 | 23.00 | 5.08 | 4892 | Normal
2015-04-30T11:51:01 | 0 | 39.00 | 23.00 | 5.10 | 4913 | Normal
2015-04-30T11:53:04 | 0 | 45.00 | 23.00 | 4.79 | 4501 | Rebooted
2015-04-30T11:53:52 | 0 | 45.00 | 23.00 | 4.77 | 4519 | Rebooted
2015-04-30T11:54:01 | 0 | 43.00 | 23.00 | 4.75 | 4501 | Rebooted
2015-04-30T15:21:01 | 0 | 41.00 | 22.00 | 4.89 | 4630 | Rebooted
2015-04-30T15:22:04 | 0 | 39.00 | 23.00 | 5.08 | 4892 | Normal
2015-04-30T15:23:04 | 0 | 38.00 | 23.00 | 5.07 | 4892 | Normal
2015-04-30T15:24:03 | 0 | 38.00 | 23.00 | 5.06 | 4871 | Normal
2015-04-30T15:25:03 | 0 | 38.00 | 23.00 | 5.05 | 4871 | Normal
2015-04-30T15:25:57 | 0 | 45.00 | 23.00 | 4.82 | 4728 | Rebooted
2015-04-30T15:26:46 | 0 | 43.00 | 23.00 | 4.37 | 4574 | Rebooted
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

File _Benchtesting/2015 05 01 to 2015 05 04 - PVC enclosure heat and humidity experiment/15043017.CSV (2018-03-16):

Time | Tips | Hum% | TempC | voltMeasure(V) | readVcc(mV) | Event
2015-04-30T11:45:17 | 0 | 48.00 | 22.00 | 5.08 | 4892 | Rebooted
2015-04-30T11:46:03 | 0 | 38.00 | 23.00 | 5.10 | 4892 | Normal
2015-04-30T11:47:02 | 0 | 40.00 | 22.00 | 5.09 | 4892 | Normal
2015-04-30T11:48:02 | 0 | 40.00 | 22.00 | 5.08 | 4913 | Normal
2015-04-30T11:49:02 | 0 | 39.00 | 23.00 | 5.10 | 4913 | Normal
2015-04-30T11:50:01 | 0 | 39.00 | 23.00 | 5.08 | 4892 | Normal
2015-04-30T11:51:01 | 0 | 39.00 | 23.00 | 5.10 | 4913 | Normal
2015-04-30T11:53:04 | 0 | 45.00 | 23.00 | 4.79 | 4501 | Rebooted
2015-04-30T11:53:52 | 0 | 45.00 | 23.00 | 4.77 | 4519 | Rebooted
2015-04-30T11:54:01 | 0 | 43.00 | 23.00 | 4.75 | 4501 | Rebooted
2015-04-30T15:21:01 | 0 | 41.00 | 22.00 | 4.89 | 4630 | Rebooted
2015-04-30T15:22:04 | 0 | 39.00 | 23.00 | 5.08 | 4892 | Normal
2015-04-30T15:23:04 | 0 | 38.00 | 23.00 | 5.07 | 4892 | Normal
2015-04-30T15:24:03 | 0 | 38.00 | 23.00 | 5.06 | 4871 | Normal
2015-04-30T15:25:03 | 0 | 38.00 | 23.00 | 5.05 | 4871 | Normal
2015-04-30T15:25:57 | 0 | 45.00 | 23.00 | 4.82 | 4728 | Rebooted
2015-04-30T15:26:46 | 0 | 43.00 | 23.00 | 4.37 | 4574 | Rebooted
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

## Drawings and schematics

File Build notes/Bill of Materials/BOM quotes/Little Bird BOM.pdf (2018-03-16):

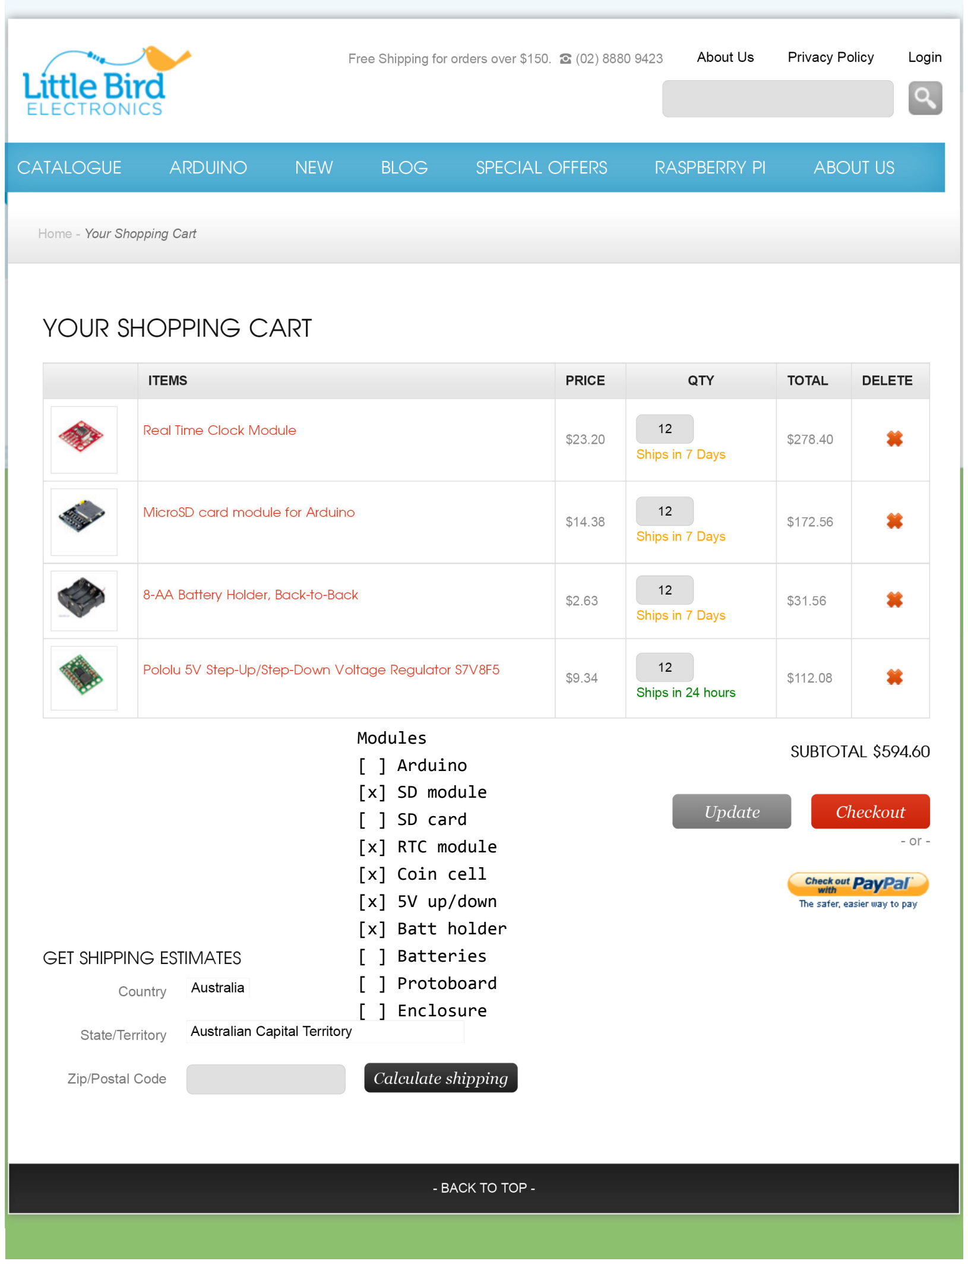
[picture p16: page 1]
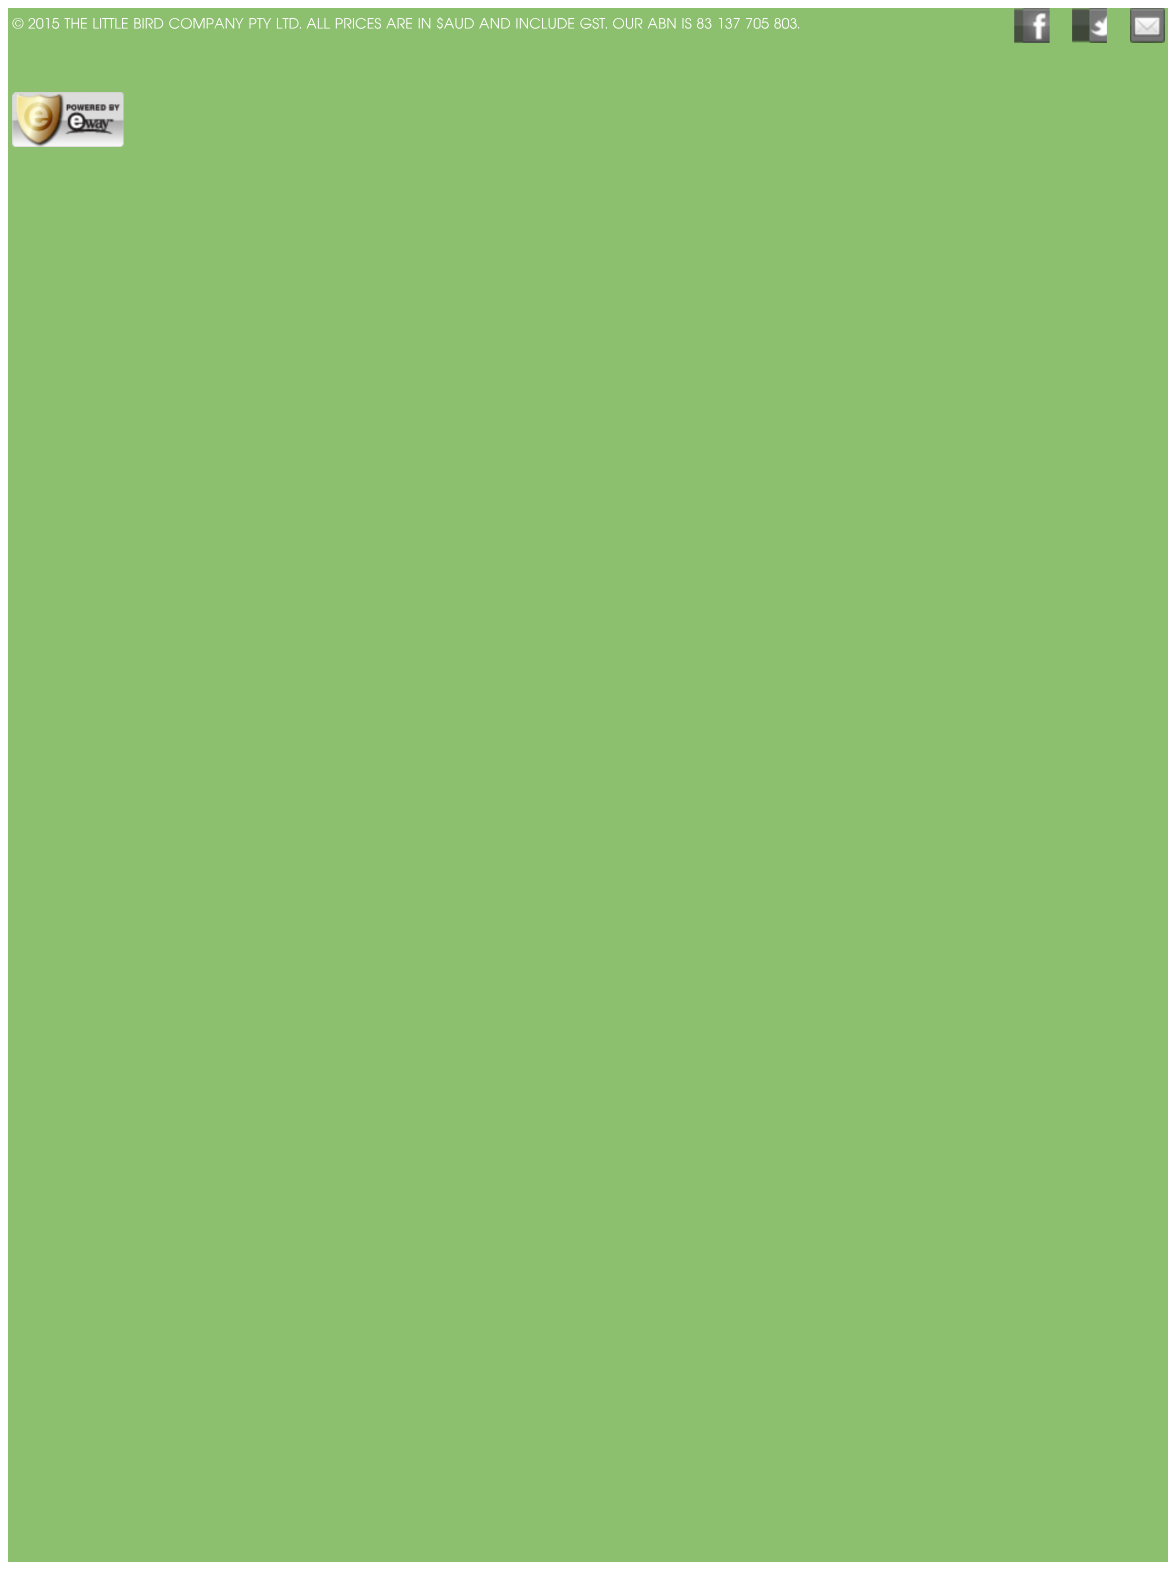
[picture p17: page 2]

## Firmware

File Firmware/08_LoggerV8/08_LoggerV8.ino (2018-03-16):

// 11 Jan 2016.
// This file is a modified version of LoggerV6.
// hasEnoughPower() now runs readVcc() twice and uses the larger of the two results.
//
// This change was made because when I graphed out the battery health of the loggers
// after 3 months of deployment, there were some anomalous voltage drops of 10—100 mV
// between log entries. By reading Vcc twice, we should be able to get around this.

// 17 Mar 2018.
// Cleaning up parts of this file because I'm sharing this project on GitHub now!
// This is just a cleaned-up version of LoggerV7 with better comments.

// #### Includes #################################################

// General includes
#include <LowPower.h>

// RTC includes
#include <Wire.h>
#include <DSRTCLib.h>

// SD includes
#include <SPI.h>
#include <SD.h>

// #### Variable initialisation ##################################

// This is the header row placed at the top of every log file.
const String headerRow = "Time,Tips,mV,Event";

volatile bool tipDetected = false;
volatile bool alarmDetected = false;

// This value is set every time hasEnoughPower() runs. This ensures that if the
// logger reads the battery voltage and decides that it's okay, that the voltage
// it used to make that decision is written to the log file.
int vccReading = 0;

int ALARM_PIN = 3;
int INT_NUMBER = 1;  // Interrupt pin
int BUZZER = 7;

DS1339 RTC = DS1339(ALARM_PIN, INT_NUMBER);

// For SD
const int chipSelect = 10;
File logFile;

// For internal logic
int TipCounter = 0;

void buzz(int PIN, int code)
{
	switch (code)
	{
	case 1: // SD access error. Beep-beeeeeep! Beep-beeeeeep!
		tone(PIN, 4978, 30);
		delay(250);
		noTone(PIN);
		tone(PIN, 4978, 120);
		delay(1000);
		noTone(PIN);
		break;
	case 2: // Power OK, bucket tip recorded. Plays after 'case 5' to make a two-toned beep.
		tone(PIN, 1000, 60);
		delay(62);
		noTone(PIN);
		break;
	case 3: // Log written. Higher-pitched single beep.
		tone(PIN, 2000, 60);
		delay(62);
		noTone(PIN);
		break;
	case 4: // All okay. Rising scale of four notes.
		tone(PIN, 1000, 60);
		delay(62);
		noTone(PIN);
		tone(PIN, 2000, 60);
		delay(62);
		noTone(PIN);
		tone(PIN, 3000, 60);
		delay(62);
		noTone(PIN);
		tone(PIN, 4000, 60);
		delay(62);
		noTone(PIN);
		break;
  case 5: // Bucket tip detected, now checking power (plays before 'case 2').
		tone(PIN, 3000, 30);
		delay(32);
		noTone(PIN);
    break;
	default: // Problem with circuit, check wiring. Insistent beeping.
		tone(PIN, 4978, 30);
		delay(250);
		noTone(PIN);
		tone(PIN, 4978, 30);
		delay(500);
		noTone(PIN);
		tone(PIN, 4978, 30);
		delay(1000);
		noTone(PIN);
		break;
	}
}

void setup()
{
	// ---- Rain collector -------------------
	pinMode(2, INPUT);
	digitalWrite(2, HIGH);
	attachInterrupt(0, recordTip, FALLING);

	// ---- Alarm setup ----------------------
	pinMode(ALARM_PIN, INPUT);
	digitalWrite(ALARM_PIN, HIGH);
	attachInterrupt(1, alarm, FALLING);

	// ---- Indicator lights -----------------
	pinMode(BUZZER, OUTPUT);
	pinMode(BUZZER, LOW);

	// ---- SD Card --------------------------
	pinMode(8, INPUT_PULLUP);
	pinMode(9, INPUT_PULLUP);
	pinMode(10, OUTPUT);

	if (!SD.begin(10))
	{
		while (true)
		{
			buzz(BUZZER, 1); // SD access error
		}
	}

	// ---- Test write -----------------------

	bool logExists = false;

	if (hasEnoughPower())
	{
		if (SD.exists("logfile.csv"))
			logExists = true;

		logFile = SD.open("logfile.csv", FILE_WRITE);

		if (logFile)
		{
			if (logExists == false)
			{
				logFile.println(headerRow); // Write a header row into a new file.
			}

			logFile.println(buildOutput("Reboot"));
			logFile.close();
		}
		else
		{
			while (true)
			{
				buzz(BUZZER, 1); // SD access error
			}
		}
	}

	// ------------------------------------------------

	Wire.begin();
	RTC.start();

	RTC.enable_interrupt();

	RTC.setMinutes(0);
	RTC.setSeconds(0);
	RTC.setAlarmRepeat(EVERY_HOUR);
	RTC.writeAlarm();

	buzz(BUZZER, 4); // All okay
}

void loop()
{
	LowPower.powerDown(SLEEP_FOREVER, ADC_OFF, BOD_OFF);

	if (tipDetected == true)
	{
		tipDetected = false;
                buzz(BUZZER, 5); // Rain detected, sounds before the power check.

                if (hasEnoughPower())
                {
        		TipCounter++;
        		buzz(BUZZER, 2); // Power OK, bucket tip added to memory
                }
	}

	if (alarmDetected == true)
	{
		RTC.clear_interrupt();
		alarmDetected = false;

		logWrite("Normal");  // Writes all memorised bucket tips to the logfile.
		TipCounter = 0;
	}
}

void recordTip()
{
  // This interrupt only triggers on a falling edge, I found that debouncing was not needed.
	tipDetected = true;
}

void alarm()
{
	alarmDetected = true;
}

String buildOutput(String eventType)
{
	String output;
	output += iso8601DateTime();
	output += ",";
	output += TipCounter;
	output += ",";
	output += vccReading;
	output += ",";
	output += eventType;
	return output;
}

String iso8601DateTime()
{
	RTC.readTime();
	String output;
	output += int(RTC.getYears());
	output += "-";
	output += withLeadingZero(int(RTC.getMonths()));
	output += "-";
	output += withLeadingZero(int(RTC.getDays()));
	output += "T";
	output += withLeadingZero(int(RTC.getHours()));
	output += ":";
	output += withLeadingZero(int(RTC.getMinutes()));
	output += ":";
	output += withLeadingZero(int(RTC.getSeconds()));
	return output;
}

String withLeadingZero(int digits)
{
	// Utility function for printing leading zeroes.
	String output;

	if (digits < 10)
		output += "0";

	output += digits;
	return output;
}

long readVcc()
{
	// Read 1.1V reference against AVcc
	// set the reference to Vcc and the measurement to the internal 1.1V reference
	// http://provideyourown.com/2012/secret-arduino-voltmeter-measure-battery-voltage/

        #if defined(__AVR_ATmega32U4__) || defined(__AVR_ATmega1280__) || defined(__AVR_ATmega2560__)
        	ADMUX = _BV(REFS0) | _BV(MUX4) | _BV(MUX3) | _BV(MUX2) | _BV(MUX1);
        #elif defined (__AVR_ATtiny24__) || defined(__AVR_ATtiny44__) || defined(__AVR_ATtiny84__)
        	ADMUX = _BV(MUX5) | _BV(MUX0);
        #elif defined (__AVR_ATtiny25__) || defined(__AVR_ATtiny45__) || defined(__AVR_ATtiny85__)
        	ADMUX = _BV(MUX3) | _BV(MUX2);
        #else
        	ADMUX = _BV(REFS0) | _BV(MUX3) | _BV(MUX2) | _BV(MUX1);
        #endif

	delay(20); // Wait for Vref to settle
	ADCSRA |= _BV(ADSC); // Start conversion
	while (bit_is_set(ADCSRA, ADSC)); // measuring

	uint8_t low = ADCL; // must read ADCL first - it then locks ADCH
	uint8_t high = ADCH; // unlocks both

	long result = (high << 8) | low;

	result = 1125300L / result; // Calculate Vcc (in mV); 1125300 = 1.1*1023*1000
	return result; // Vcc in millivolts
}

bool hasEnoughPower()
{
	// This function checks whether the available power is at least 3.2 V (the TinyDuino's microSD shield needs at least 3.0 V
  // to safely operate. This should get called as a condition for every SD card access.
  //
  // Originally set to a 2800 mV threshold, but the RTC got really sketchy as it got close to 3.0 V and brownout.
  // During bench testing I got a drop of only 600 mV after 36 days, logging once every minute, so based on these data it would
  // take 4 months to drop to 3100 mV. And since the field units are going to have two 3xAA battery packs in parallel (the test
  // unit has only one pack), it will take even longer to drop to that level. The standard deviation of these readings is 134 mV,
  // so I'm increasing this safety margin from 3000 mV to 3200 mV juuuuuuuust in case.

  int tempVcc1 = int(readVcc());
  int tempVcc2 = int(readVcc());

  if (tempVcc1 > tempVcc2)
  {
      vccReading = tempVcc1;
  }
  else
  {
      vccReading = tempVcc2;
  }

	if (vccReading >= 3200)
		return true;
	else
		return false;
}

void logWrite(String eventType)
{
	if (hasEnoughPower())
	{
		logFile = SD.open("logfile.csv", FILE_WRITE);

		if (logFile)
		{
      // I have noticed that the Vcc recorded in the log is different from the Vcc that hasEnoughPower() found.
      // Could be ADC settling time or could be the fact that the SD module is being accessed. That's why I now
      // set a global vccReading variable instead of accessing readvcc() again for the log entry.

			logFile.println(buildOutput(eventType));
			logFile.close();
		        buzz(BUZZER, 3); // Log written
		}
		else
		{
			buzz(BUZZER, 1); // SD access error
		}
	}
}

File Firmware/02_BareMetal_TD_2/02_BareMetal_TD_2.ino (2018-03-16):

#pragma region "#### Includes #################################################"

// General includes
#include <LowPower.h>
#include <JeeLib.h>

// RTC includes
#include <Wire.h>
#include <DSRTCLib.h>

// SD includes
#include <SPI.h>
#include <SD.h>

// Sensor includes
#include <dht.h>

#pragma endregion

#pragma region "#### Variable initialisation ##################################"

// This is the header row placed at the top of every log file.
const String headerRow = "Time,Tips,Hum%,TempC,mV,Event";

// For error lights
#define LEDPIN 7 // I can't use the built-in LED because it is involved in SPI for the SD shield.

// For RTC
DS1339 RTC = DS1339(3, 1); // Interrupt pin D3, Interrupt number 1 (pin 3).
volatile bool alarmTriggered = false;
#define ALARMPIN 3

// For rain collector
#define RAINPIN 2

// For SD
const int chipSelect = 10;
File logFile;

// For DHT11
#define dht_dpin A0
dht DHT;

// For internal logic
int TipCounter = 0;
volatile bool tipEventDetected = false;
unsigned long timeOfLastTip = 0;

#pragma endregion

// #### Setup ####################################################

/*
	Error codes (Flashing LED on pin 9):

	Fast x3			RTC couldn't be initialised.
	Fast-slow		SD card couldn't be initialised.
	Slow-slow		Couldn't access DHT11.
	2 fast 5 Slow	All OK, starting to log data.
*/

void setup ()
{
	// ---- Error LED ------------------------
  
	pinMode(LEDPIN, OUTPUT);
	digitalWrite(LEDPIN, LOW);
  
	// ---- Rain collector -------------------
  
	pinMode(RAINPIN, OUTPUT);
	digitalWrite(RAINPIN, HIGH); // When the switch closes, this pin gets pulled low.
  
	// ---- SD Card --------------------------
  
	pinMode(8, INPUT_PULLUP);
	pinMode(9, INPUT_PULLUP);
	pinMode(10, OUTPUT);
  
	// ---- DHT 11 package -------------------
  
	delay(1000);
	DHT.read11(dht_dpin);
	if (DHT.humidity == 0)
	{
		while (true)
		{
		  // Stop running and do slow long-long blinks.
		  ledBlink(LEDPIN, 10, 750, 750, 750, 750);
		}
	}
  
	// ---- Alarm ----------------------------
  
	pinMode(ALARMPIN, INPUT);
	digitalWrite(ALARMPIN, HIGH);
  
	// ---- RTC ------------------------------
  
	Wire.begin();
	RTC.start();
  
	// Set the time by running the Set_TinyDuino_Time sketch.
  
	if (!RTC.time_is_set()) {
		while (true)
		{
			// Stop running and just blink the LED fast-fast-fast.
			ledBlink(LEDPIN, 3, 100, 100, 100, 100);
			Sleepy::loseSomeTime(200);
		}
	}

	// ---- Timekeeping ----------------------
  
	timeOfLastTip = millis();
  
	// ---- SD card --------------------------
  
	if (!SD.begin(10))
	{
		while (true)
		{
			// Stop running and do short-long-short-long blinks.
			ledBlink(LEDPIN, 10, 100, 100, 500, 100);
		}
	}

	// ---- Test write -----------------------
  
	bool logExists = false;
  
	if (hasEnoughPower())
	{
		if (SD.exists("logfile.csv"))
			logExists = true;
	
		logFile = SD.open("logfile.csv", FILE_WRITE);
	
		if (logFile)
		{
			if (logExists == false)
			{
				ledBlink(LEDPIN, 1, 100, 50, 100, 50);
				logFile.println(headerRow); // Write a header row into a new file.
			}
	  
			logFile.println(buildOutput("Rebooted"));
			logFile.close();
		}
		else
		{
			while (true)
			{
				// Stop running and do short-long-short-long blinks.
				ledBlink(LEDPIN, 10, 100, 100, 750, 100);
			}
		}
	}
  
	// ---- Self-tests complete --------------
  
	// Give us some visual indication that everything is okay.
	ledBlink(LEDPIN, 5, 500, 100, 500, 100);
  
	// ---- Prepare external interrupts ------
	attachInterrupt(0, recordTip, LOW);
	attachInterrupt(1, alarm, FALLING);
	RTC.enable_interrupt();
	RTC.setAlarmRepeat(EVERY_MINUTE);
	RTC.setSeconds(0);
	RTC.writeAlarm();
}

// #### Main loop ################################################

void loop ()
{
	LowPower.powerDown(SLEEP_FOREVER, ADC_OFF, BOD_OFF);
  
	if (tipEventDetected == true)
	{
		ledBlink(LEDPIN, 4, 250, 250, 250, 250);
		// Oh, I got tipped while I was sleeping! Better write that down.
		TipCounter++;
		tipEventDetected = false;
	}
  
	if (alarmTriggered == true)
	{
		RTC.clear_interrupt();
		ledBlink(LEDPIN, 8, 250, 250, 250, 250);
		// It's a new minute! I can write data! \o/
		logWrite("Normal");
		TipCounter = 0;
		alarmTriggered = false;
	}
}

// #### Function declarations ####################################

// ---- Utility functions ----------------
// I've gotta organise myself with a TOC because Arduino IDE doesn't have code folding! It's 2015, man!
//	1. void	recordTip()
//	2. String  buildOutput(String eventType)
//	3. String  iso8601DateTime()
//	4. String  withLeadingZero(int digits)
//	5. bool	hasEnoughPower()
//	6. void	ledBlink(int ledPinLocation, int flashes, int evenOn, int evenOff, int oddOn, int oddOff)
//	7. long	readVcc()
//	8. float   voltMeasure()

void recordTip()
{
	int timeDifference = int(abs(millis() - timeOfLastTip));
  
	if (timeDifference >= 2000)
	{
		tipEventDetected = true;
		timeOfLastTip = millis();
	}
}

void alarm()
{
	alarmTriggered = true;
}


String buildOutput(String eventType)
{
	delay(1000);
	DHT.read11(dht_dpin);
  
	String output;
	output += iso8601DateTime();
	output += ",";
	output += TipCounter;
	output += ",";
	output += DHT.humidity;
	output += ",";
	output += DHT.temperature;
	output += ",";
	output += readVcc();
	output += ",";
	output += eventType;
	return output;
}

String iso8601DateTime()
{
	RTC.readTime();
	String output;
	output += int(RTC.getYears());
	output += "-";
	output += withLeadingZero(int(RTC.getMonths()));
	output += "-";
	output += withLeadingZero(int(RTC.getDays()));
	output += "T";
	output += withLeadingZero(int(RTC.getHours()));
	output += ":";
	output += withLeadingZero(int(RTC.getMinutes()));
	output += ":";
	output += withLeadingZero(int(RTC.getSeconds()));
	return output;
}

String withLeadingZero(int digits)
{
	// Utility function for printing leading zeroes.
	String output;
  
	if (digits < 10)
		output += "0";

	output += digits;
	return output;
}

bool hasEnoughPower()
{
	// This function checks whether the available power is at least 2.8 V, which is what the TinyDuino's microSD shield needs to safely operate.
	// This should get called as a condition for every SD card access.
  
	if (int(readVcc()) >= 2800)
		return true;
	else
		return false;
}
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

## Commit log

2018-03-16 Initial commit.
    [15043016.CSV, 15043017.CSV, 15043018.CSV, 15043019.CSV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]
2018-03-16 Added more documentation.
    [Circuit - Datalogger v6.fzz, Circuit - Datalogger v8.fzz]
2018-03-16 More doc changes
    [15043016.CSV, 15043017.CSV, 15043018.CSV, 15043019.CSV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]
